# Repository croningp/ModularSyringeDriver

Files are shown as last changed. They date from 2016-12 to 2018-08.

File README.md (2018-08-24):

# Modular Syringe Driver
Welcome to the Modular Syringe Driver repository! Here, you will find all the necessary information to create your own version of this device.

Here is the finished product:

Alt img

All designs are hosted on Onshape:
* [Syringe Driver](https://cad.onshape.com/documents/56ab4447e4b0dff6d869c7ac/w/10403a3c4431f66501924e81/e/ad868b310df8ef7bb56f2516)
* [Modularity](https://cad.onshape.com/documents/20421eb13def16ddb65f3155/w/9ed7d19760b1ecfa0f48b9ff/e/2a6517c7e659cf206dda40c0)

For a list of all the materials you will need, please see the [Materials](hardware/materials.md) documentation.
* Note: A 3D printer is required to obtain some of these materials.

## Modularity
The appeal of this device is its modularity. Many different additions can be designed and printed for this device.
Here are a few examples of possible additions:



## Dependencies
* [Commanduino](https://github.com/croningp/commanduino)
* [Arduino CommandHandler](https://github.com/croningp/Arduino-CommandHandler)
* [Arduino CommandTools](https://github.com/croningp/Arduino-CommandTools)

## Assembly
Please see the the [Assembly](hardware/assembly.md) documentation for information on assembly.

## Example Usage
Below is an example of how to use [commanduino](https://github.com/croningp/commanduino) to communicate with the syringe driver.
Here we import the CommandManager which is used to communicate with the hardware via Arduino.
We also import the Axis device from Commanduino which allows the syringe to be placed on an XY axis for independent movement.

Variables are set up for the individual components of the driver, such as how many mm/step the motor should move, and the maximum volume of the syringe etc.
Instantiating an Axis object with the stepper information and passing it to the Syringe allows us full access to the Syringe commands.

See the [Syringe software](software/syringe.py) for more information on the syringe commands. 

JSON Example for setting up the Linear Accelerator Actuator in commanduino:
```json

{
  "ios" : [
    {
      "port": "/dev/tty.usbmodem1411"
    },
    {
      "port": "/dev/ttyACM0"
    },
    {
      "port": "/dev/ttyACM1"
    },
    {
      "port": "/dev/ttyACM2"
    }
  ],
  "devices": {
    "stepper": {
      "command_id": "LS1",
      "config": {
        "enabled_acceleration": false,
        "speed": 1000,
        "max_speed": 1000,
        "acceleration": 1000
      }
    }
  }
}
```

Python code for setting up the Syringe Driver: 

``` python
from commanduino import CommandManager
from commanduino.devices.axis import Axis
from syringe import Syringe

configfile = os.path.join(HERE_PATH, 'robot_config.json')
cmdMng = CommandManager.from_configfile(configfile)

MICROSTEP = 32.0
LINEAR_STEPPER_UNIT_PER_STEP = 0.05  # mm/step
SYRINGE_UNIT_PER_MM = 250 / 59.70  # 59.70mm for 250ul
SYRINGE_MAX = 235
SYRINGE_AXIS = Axis(cmdMng.S1, LINEAR_STEPPER_UNIT_PER_STEP * SYRINGUE_UNIT_PER_MM / MICROSTEP, 0, SYRINGE_MAX)
SYRINGE = Syringe(SYRINGE_AXIS, SYRINGE_MAX)
```

## Authors

Design and code by [Jonathan Grizou](http://www.chem.gla.ac.uk/cronin/members/Jonathan/), documentation by [Graham Keenan](https://github.com/ShinRa26), while working in the [Cronin Group](http://www.chem.gla.ac.uk/cronin/).

## Licenses

|   License     |     Hardware    |   Software      |
| ------------- | :-------------: | :-------------: |
| Title  | [Creatives Commons BY-SA](http://creativecommons.org/licenses/by-sa/4.0/)  |[GPL v3](http://www.gnu.org/licenses/gpl.html)  |
| Logo  |   |GPL V3 (http://www.gnu.org/licenses/gpl.html)  |

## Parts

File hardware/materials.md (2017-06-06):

# Bill of Materials
These are the materials needed to create the modular syringe driver and where to source them.

## Screws & Quantities
Screw | Quantity | Vendor
--- | --- | ---
M2.5 x 6mm | 6 | [RS Components](http://uk.rs-online.com/web/p/socket-screws/4838124/)
M3 x 6mm | 5 | [RS Components](http://uk.rs-online.com/web/p/socket-screws/1871207/)
M2.5 x 12mm | 5 | [RS Components](http://uk.rs-online.com/web/p/socket-screws/4838130/)
M3 x 10mm | 2 | [RS Components](http://uk.rs-online.com/web/p/socket-screws/2328366/)
M3 x 12mm | 4 | [RS Components](http://uk.rs-online.com/web/p/socket-screws/1871229/)

## Stepper Motor

The stepper motor used is a [custom-made Nema 11](custom_stepper/), sourced from Heason (This is the preferred motor for this setup).

Contact [Paul Sorrell](mailto:psorrell@heason.com) for more information.

Alternative motor from [Stepper Online](http://www.omc-stepperonline.com/threaded-rod-nema-11-external-linear-stepper-motor34mm-body-100mm-t5-x-2-p-203.html):



## Stop Switch
The switch used on the syringe driver is a D2F Ultra Subminature Basic Switch, sourced from [Omron](http://uk.farnell.com/omron-electronic-components/d2f01lt/microswitch-hinge-lever-0-1/dp/1961085)

[Data Sheet](https://www.omron.com/ecb/products/pdf/en-d2f.pdf) for the D2F switch.

## Arduino Mega + RAMPS Shield
The syringe driver is controlled via an Arduino Mega 2560 board fitted with a RAMPS v1.4 shield.

* The Arduino Mega can be sourced from the [Arduino website](https://www.arduino.cc/en/Main/ArduinoBoardMega2560) or from many electronics retailers.


* The RAMPS v1.4 shield can be sourced from [Ooznest](http://ooznest.co.uk/RAMPS-14-Controller-Board-Premium&currency=GBP&language=en?gclid=Cj0KEQiAyuPCBRCimuayhb3qqvwBEiQAgz62kVp1GNCQKYvTIFOcvpG9ZQ0eJvKzC2Tw6_trZBFtpCMaAlxl8P8HAQ)


## Stepper Motor Drivers for RAMPS v1.4
The stepper drivers used to control the stepper motor are [DRV8825 Drivers](https://www.pololu.com/product/2982)


Here is a video on how to tune the driver to deliver the desired Amperage: https://www.youtube.com/watch?feature=player_embedded&v=89BHS9hfSUk

## Linear Guide Rail
The syringe is guided by a linear rail, sourced at [RS Components](http://uk.rs-online.com/web/p/linear-guides-rails/6192391/)


## Linear Guide Carraige
Attached to the linear rail is a guide carraige, also sourced at [RS Components](http://uk.rs-online.com/web/p/linear-guides-guide-blocks-carriages/6192442/)


## 3D Prints
Many of the parts needed to create this driver can be 3D printed. Please see the [Basic Driver](basic_driver_stls/) and [Modular Additions](modular_additions_stls/) folders for the appropriate STL files.

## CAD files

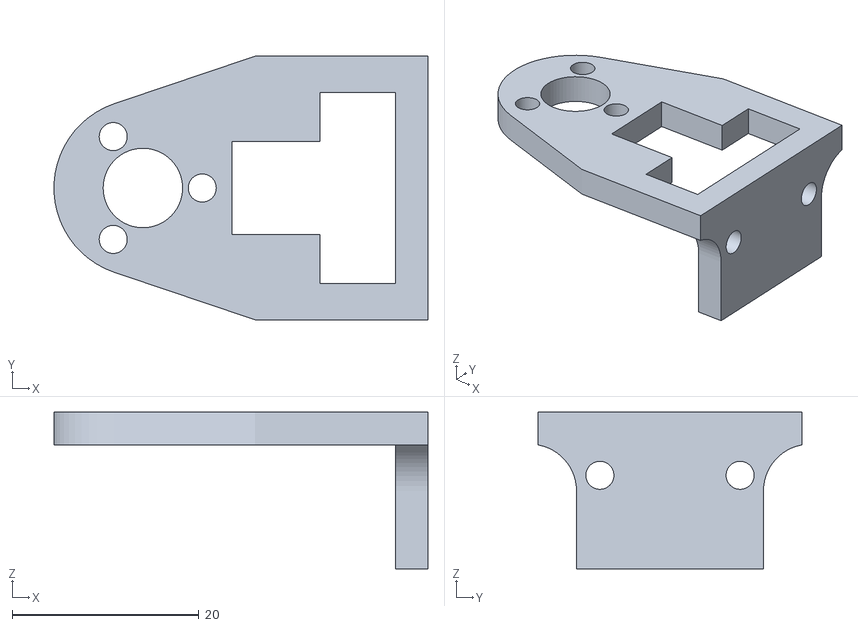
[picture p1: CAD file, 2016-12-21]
hardware/basic_driver_stls/Syringe_Holder_Carriage.stl
40.0 x 28.2 x 16.8

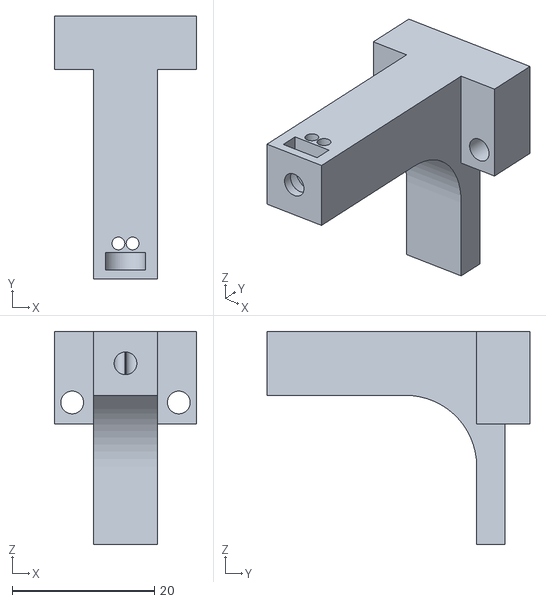
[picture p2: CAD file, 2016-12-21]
hardware/modular_additions_stls/cleaning_addon/Cleaning_Mount.stl
20.0 x 37.0 x 30.0

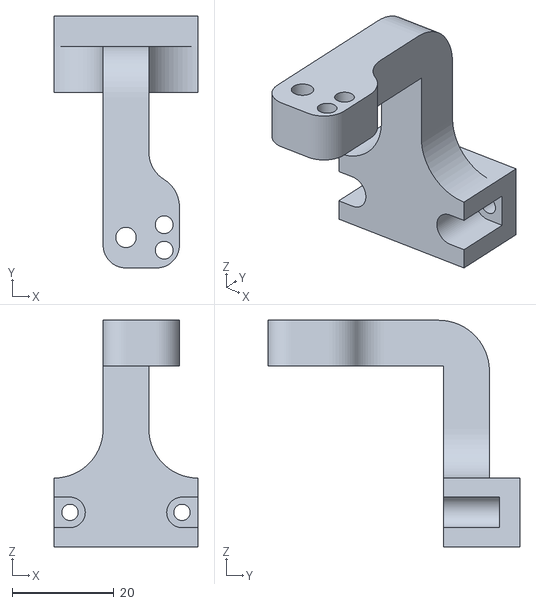
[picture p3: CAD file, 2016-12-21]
hardware/modular_additions_stls/guide_addon/Guide_v2.stl
28.2 x 49.5 x 44.5

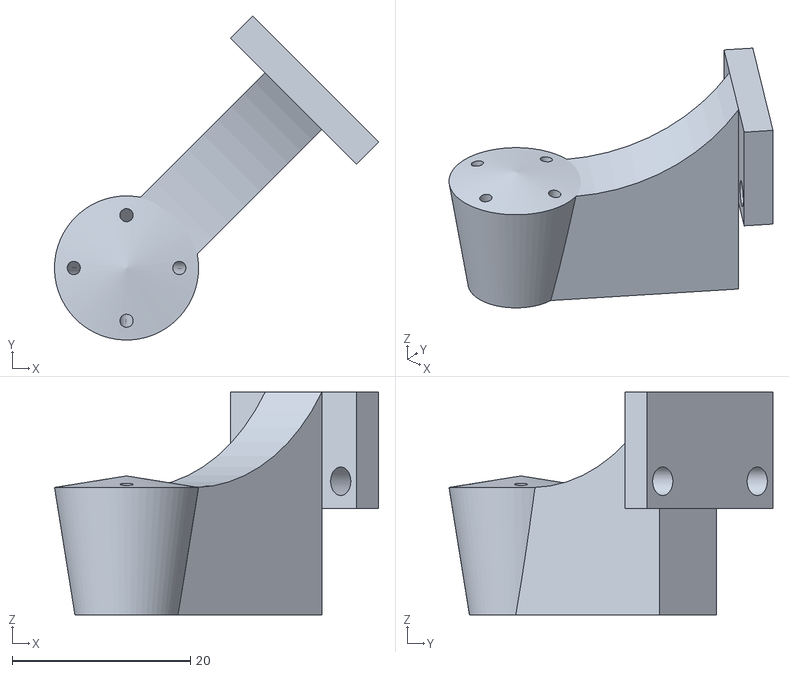
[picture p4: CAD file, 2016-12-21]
hardware/modular_additions_stls/oil_station_addon/precision_station.stl
36.4 x 36.4 x 25.0

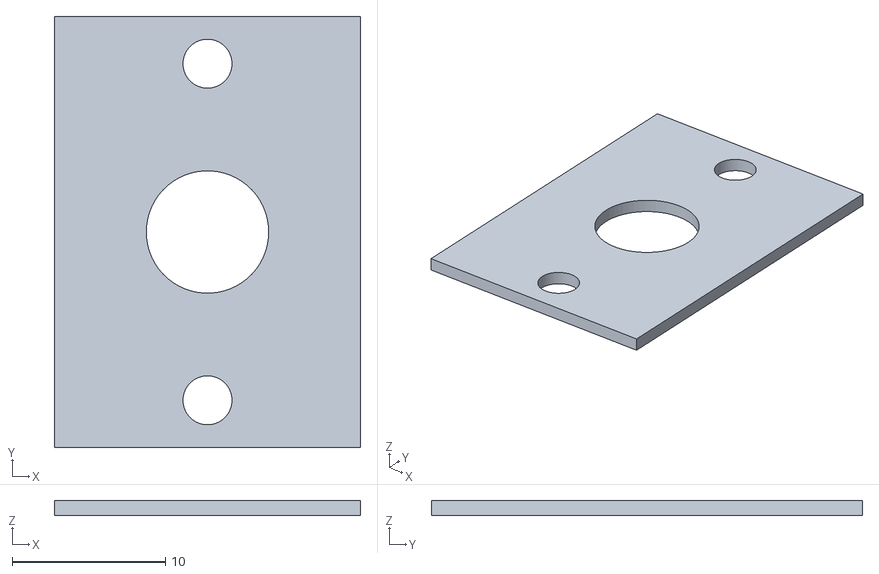
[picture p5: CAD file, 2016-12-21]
hardware/modular_additions_stls/syringe_addon/Syringe_Cover_Bottom.stl
20.0 x 28.2 x 1.00

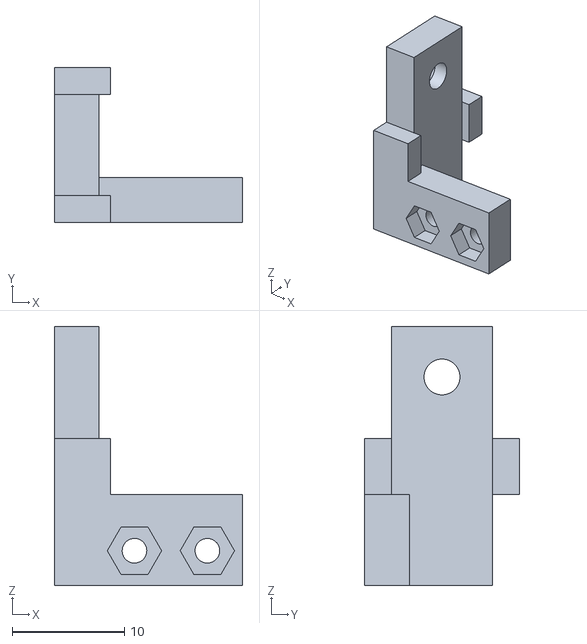
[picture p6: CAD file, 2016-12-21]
hardware/basic_driver_stls/microswitch_bracket.stl
16.8 x 13.8 x 23.1

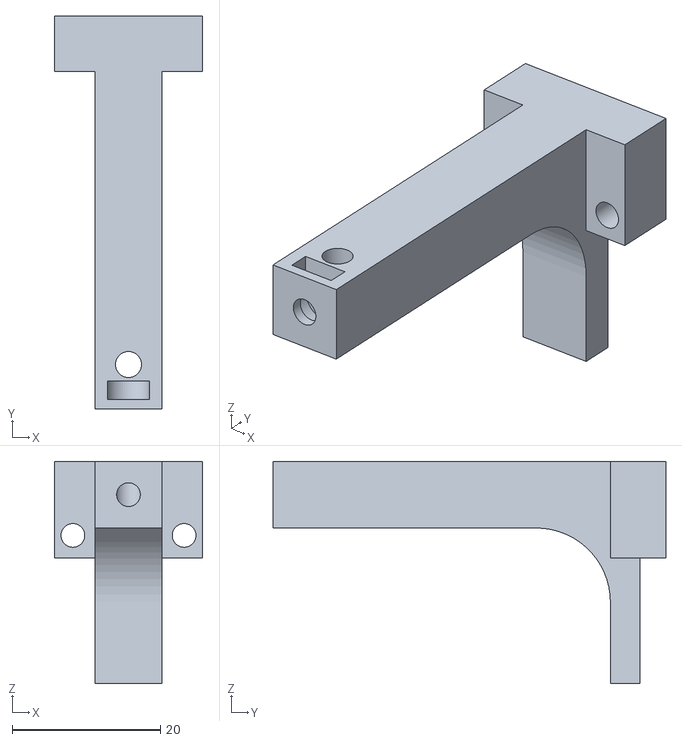
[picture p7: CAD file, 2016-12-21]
hardware/modular_additions_stls/cleaning_addon/Cleaning_mount_v2.stl
20.0 x 53.0 x 30.0

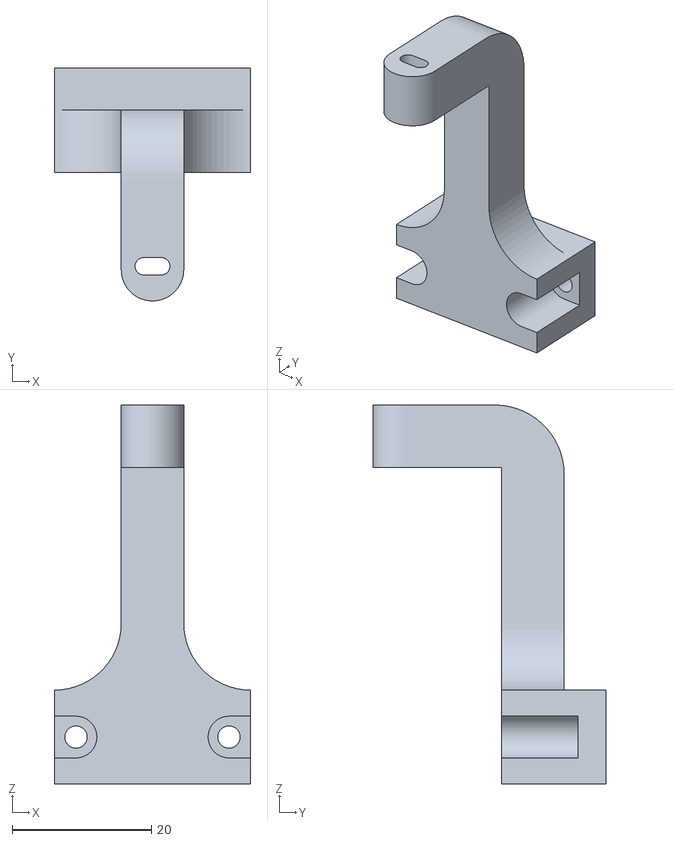
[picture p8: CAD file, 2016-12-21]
hardware/modular_additions_stls/guide_addon/Guide.stl
28.2 x 33.5 x 54.5

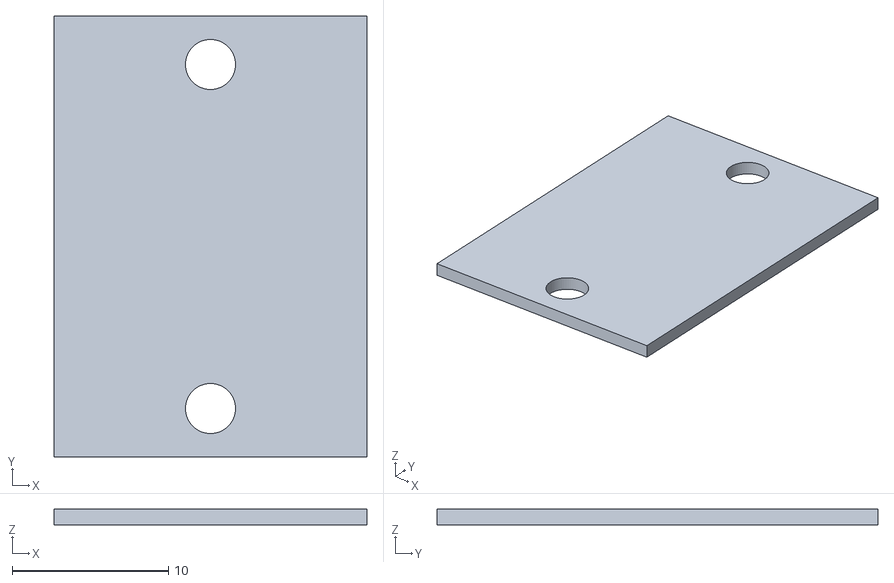
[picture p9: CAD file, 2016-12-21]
hardware/modular_additions_stls/syringe_addon/Syringe_Cover_Top.stl
20.0 x 28.2 x 1.00

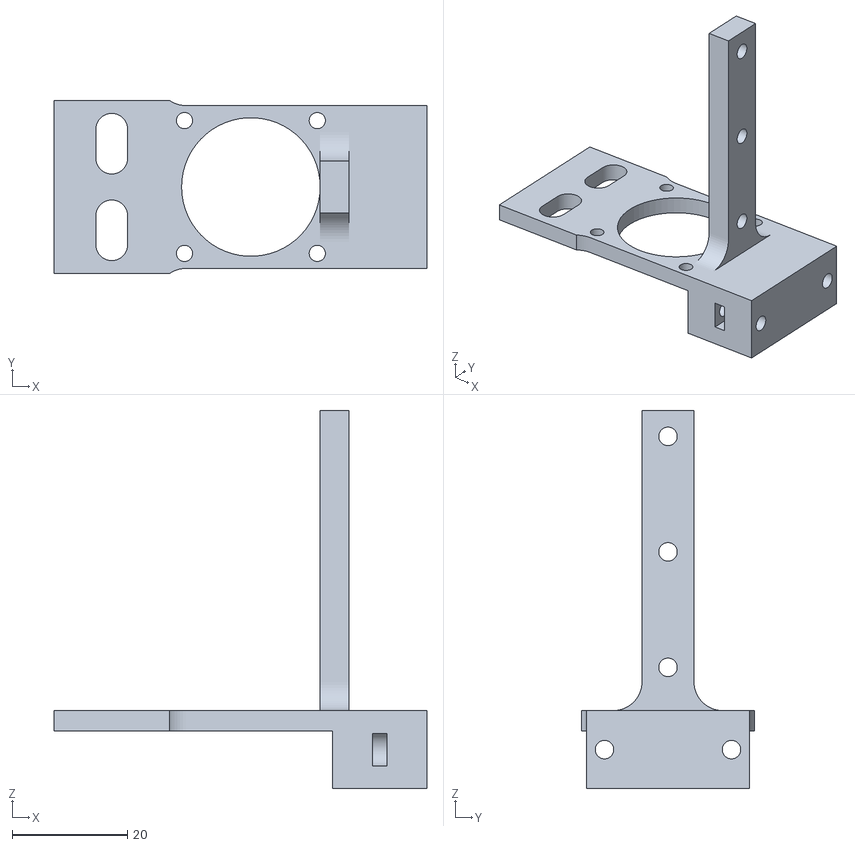
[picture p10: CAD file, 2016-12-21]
hardware/basic_driver_stls/Syringe_base.stl
64.6 x 30.0 x 65.5

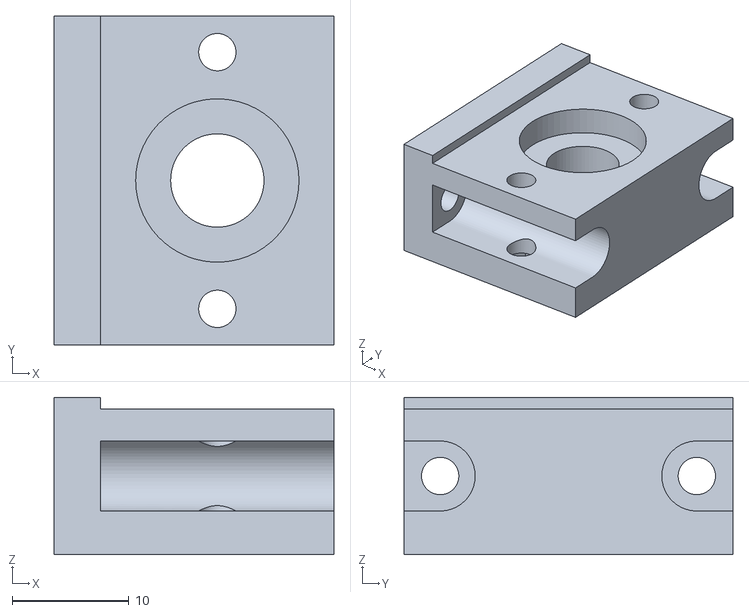
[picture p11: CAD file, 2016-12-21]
hardware/modular_additions_stls/syringe_addon/Syringe_Holder_Bottom.stl
24.0 x 28.2 x 13.5

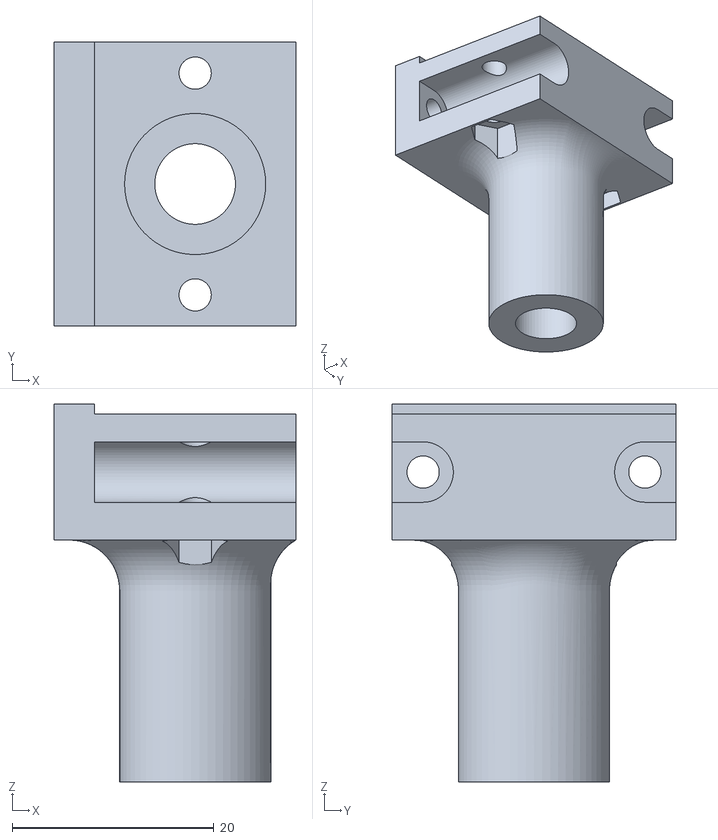
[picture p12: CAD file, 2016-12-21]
hardware/modular_additions_stls/syringe_addon/Syringe_Holder_Bottom_Extended.stl
24.0 x 28.2 x 37.5

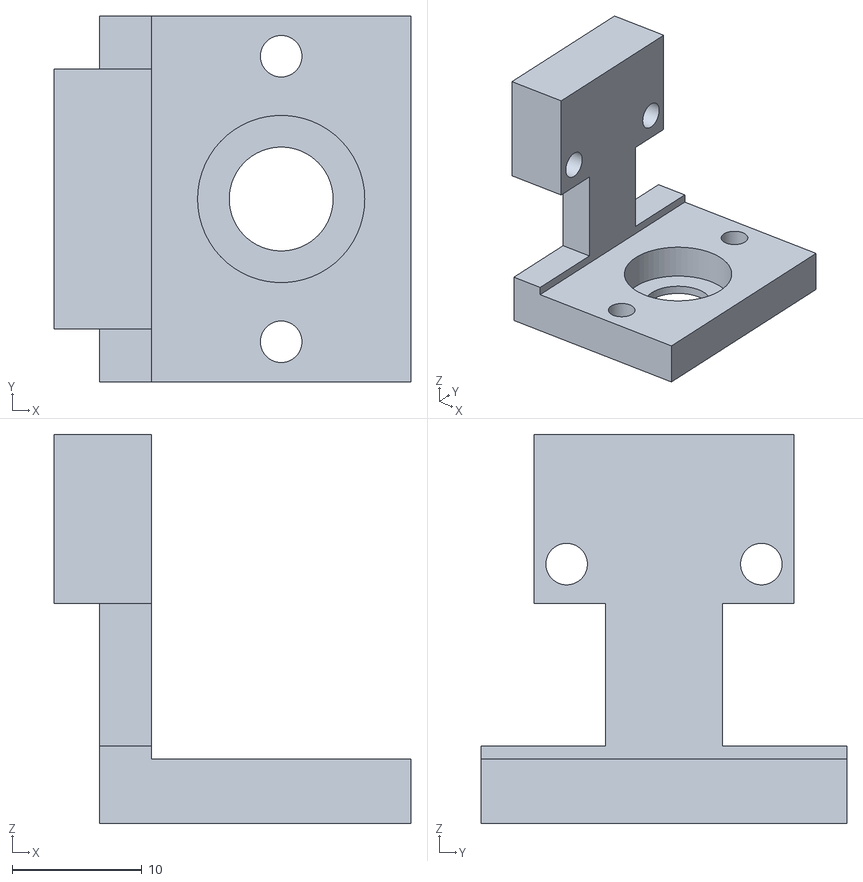
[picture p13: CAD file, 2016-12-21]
hardware/modular_additions_stls/syringe_addon/Syringe_puller.stl
27.5 x 28.2 x 30.0

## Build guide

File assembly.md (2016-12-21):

# Assembly of the Modular Syringe Driver
This purpose of this guide is to explain how to assemble the basic syringe driver.

## What you will need
In addition to the items listed in the [materials](hardware/materials.md) documentation, you will also need:

* 6x M2.5 6mm Screws 
* 5x M3 6mm Screws
* 5x M2.5 12mm Screws
* 2x M3 10mm Screws
* 4x M3 12mm Screws
* Appropriately-sized nuts for each screw type

## Part 1: Attaching the base to the motor
Requirements:
* 4x M2.5 6mm Screws
* Driver Base



Start by placing the base on top of the stepepr motor with the wires perpendicular to the base:


Screw the base onto the stepper motor:


## Part 2: Attaching the Rail + Guide
Requirements:
* 3x M3 6mm Screws
* 3x M3 Nuts
* Rail
* Rail Guide



Place the Rail against the vertical post, like so:


Add the nuts to the divots and screw in place:


Next, carefully add the Rail Guide to the rail:


## Part 3: Attaching the Frame to the Rail Guide
Requirements:
* 2x M3 6mm Screws
* Frame



Slide the frame over the rail with the vertical portion facing downwards, like so:


Screw the frame onto the bottom section of the Rail Guide


## Part 4: Securing the Frame onto the Threaded Guide:
Requirements:
* 3x M2.5 12mm Screws
* 3x M2.5 Nuts

Raise the threaded guide on the motor:


Add the screw and secure with a nut, like so:


Do this for the remaining two slots:


## Part 5: Addition of the Syringe Holder (Top)
Requirements:
* 2x M3 10mm Screws
* Syringe Holder (Top Portion)



Secure the syringe holder to the top portion of the Rail Guide, like so:


## Part 6: Addition of the Syringe Holder (Bottom)
Requirements:
* 2x M3 16mm Screws
* 2x M3 Nuts
* Syringe Holder (Bottom Portion)



Insert the two nuts into the slots on the base, added in **Part 1**


Insert the screws into the Syringe Holder:


Screw the Syringe Holder to the base:


## Part 7: Addition of the Switch
* 2x M2.5 12mm Screws
* 2x M2.5 Nuts
* Switch
* Switch Holding Bracket



Add the two nuts into the divots on the Switch Holding Bracket:


Add the two screws to the Switch:


Screw in place:


## Part 7.5: Attaching the Switch to the Rail
Requirements:
* Switch prepared from **Part 7**
* 1x M3 6mm Screw
* 1x M3 Nut



Similar to **Part 2**, attach the switch bracket to the top of the Rail:


## Part 8: Addition of the Syringe Cover (Bottom)
Requirements:
* Syringe
* Syringe Cover
* 2x M3 16mm Screws
* 2x M3 Nuts



Add the syringe - remove the plunger first - to the Holder:
**NOTE:** You may have to remove the Syringe Holder (**Part 5**) in order to fit the syringe into the holder in this section.


Add the cover:


Add the nuts to the divots on the bottom of the holder and crew in place, like so:


## Part 9: Addition of the Syringe Cover (Top)
Requirements:
* Syringe Cover (Top)
* Syringe plunger
* 2x M2.5 6mm Screws
* 2x M2.5 Nuts



Insert the plunger through the top of the Syringe Holder (Ensure the plunger is inline witht he Syringe!):


Add the Syringe Cover:


Add the nuts and screw in place:


**That's all there is to it!**

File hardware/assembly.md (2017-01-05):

# Assembly of the Modular Syringe Driver
This purpose of this guide is to explain how to assemble the basic syringe driver.

## What you will need
Please see [Bill of Materials](materials.md) for detailed listing.

Item | Quantity | Vendor
--- | --- | ---
M2.5 x 6mm Screw | 6 | [RS Components](http://uk.rs-online.com/web/p/socket-screws/4838124/)
M3 x 6mm Screw | 5 | [RS Components](http://uk.rs-online.com/web/p/socket-screws/1871207/)
M2.5 x 12mm Screw | 5 | [RS Components](http://uk.rs-online.com/web/p/socket-screws/4838130/)
M3 x 10mm Screw | 2 | [RS Components](http://uk.rs-online.com/web/p/socket-screws/2328366/)
M3 x 12mm Screw | 4 | [RS Components](http://uk.rs-online.com/web/p/socket-screws/1871229/)
Stepper Motor | 1 | See [Bill of Materials](materials.md)
Microswitch | 1 | [Omron](http://uk.farnell.com/omron-electronic-components/d2f01lt/microswitch-hinge-lever-0-1/dp/1961085)
Arduino Mega 2560 | 1 | [Arduino.cc](https://www.arduino.cc/en/Main/ArduinoBoardMega2560)
RAMPS v1.4 Shield | 1 | [Ooznest](http://ooznest.co.uk/RAMPS-14-Controller-Board-Premium&currency=GBP&language=en?gclid=Cj0KEQiAyuPCBRCimuayhb3qqvwBEiQAgz62kVp1GNCQKYvTIFOcvpG9ZQ0eJvKzC2Tw6_trZBFtpCMaAlxl8P8HAQ)
DRV8825 Stepper Driver | 1 | [Pololu](https://www.pololu.com/product/2982)
Linear Guide Rail | 1 | [RS Components](http://uk.rs-online.com/web/p/linear-guides-rails/6192391/)
Linear Guide Carriage | 1 | [RS Components](http://uk.rs-online.com/web/p/linear-guides-guide-blocks-carriages/6192442/)
3D Prints | 1x Each | [Basic Driver STLs](basic_driver_stls/), [Modular Addition STLs](modular_addition_stls/)

## Part 1: Attaching the base to the motor
Requirements:
* 4x M2.5 6mm Screws
* Driver Base



Start by placing the base on top of the stepepr motor with the wires perpendicular to the base:


Screw the base onto the stepper motor:


## Part 2: Attaching the Rail + Guide
Requirements:
* 3x M3 6mm Screws
* 3x M3 Nuts
* Rail
* Rail Guide



Place the Rail against the vertical post, like so:


Add the nuts to the divots and screw in place:


Next, carefully add the Rail Guide to the rail:


## Part 3: Attaching the Frame to the Rail Guide
Requirements:
* 2x M3 6mm Screws
* Frame



Slide the frame over the rail with the vertical portion facing downwards, like so:


Screw the frame onto the bottom section of the Rail Guide


## Part 4: Securing the Frame onto the Threaded Guide:
Requirements:
* 3x M2.5 12mm Screws
* 3x M2.5 Nuts

Raise the threaded guide on the motor:


Add the screw and secure with a nut, like so:


Do this for the remaining two slots:


## Part 5: Addition of the Syringe Holder (Top)
Requirements:
* 2x M3 10mm Screws
* Syringe Holder (Top Portion)



Secure the syringe holder to the top portion of the Rail Guide, like so:


## Part 6: Addition of the Syringe Holder (Bottom)
Requirements:
* 2x M3 16mm Screws
* 2x M3 Nuts
* Syringe Holder (Bottom Portion)



Insert the two nuts into the slots on the base, added in **Part 1**


Insert the screws into the Syringe Holder:


Screw the Syringe Holder to the base:


## Part 7: Addition of the Switch
* 2x M2.5 12mm Screws
* 2x M2.5 Nuts
* Switch
* Switch Holding Bracket



Add the two nuts into the divots on the Switch Holding Bracket:


Add the two screws to the Switch:


Screw in place:


## Part 7.5: Attaching the Switch to the Rail
Requirements:
* Switch prepared from **Part 7**
* 1x M3 6mm Screw
* 1x M3 Nut



Similar to **Part 2**, attach the switch bracket to the top of the Rail:


## Part 8: Addition of the Syringe Cover (Bottom)
Requirements:
* Syringe
* Syringe Cover
* 2x M3 16mm Screws
* 2x M3 Nuts



Add the syringe - remove the plunger first - to the Holder:
**NOTE:** You may have to remove the Syringe Holder (**Part 5**) in order to fit the syringe into the holder in this section.


Add the cover:


Add the nuts to the divots on the bottom of the holder and crew in place, like so:


## Part 9: Addition of the Syringe Cover (Top)
Requirements:
* Syringe Cover (Top)
* Syringe plunger
* 2x M2.5 6mm Screws
* 2x M2.5 Nuts



Insert the plunger through the top of the Syringe Holder (Ensure the plunger is inline witht he Syringe!):


Add the Syringe Cover:


Add the nuts and screw in place:


To ensure the nuts are secured in place, add some Screw Lock glue to the nuts:


## Cabling the Microswitch
* The convention for the Microswitch is:
    * Red: 5v
    * Black: Ground
    * Blue: Signal



The order, from left to right, is as follows:
* Left Pin: Blue(Signal)
* Middle Pin: Black (Ground)
* Right Pin: Red (5v Power)



## Cabling the Stepper Motor
* The stepper motor comes with 4 wires:
    * Red
    * Red/White
    * Green
    * Green/White

To connect them to the ramps shield, the convention is as follows (Motor -> RAMPS connector):
* Red/White -> Black
* Red -> Green
* Green/White -> Red
* Green -> Blue

Example:


Attaching to the RAMPS shield (also applies to the Microswitch):


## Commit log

2016-12-20 Added the bill of materials
2016-12-21 First pass
    [Cleaning_Mount.stl, Cleaning_mount_v2.stl, Guide.stl, Guide_v2.stl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]
2016-12-21 Minor changes
    [Cleaning_Mount.stl, Cleaning_mount_v2.stl, Guide.stl, Guide_v2.stl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]
2016-12-21 Minor updates
    [Syringe_Cover_Bottom.stl, Syringe_Cover_Top.stl, Syringe_Holder_Bottom.stl, Syringe_Holder_Bottom_Extended.stl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]
2017-01-05 Added the wiring and JSON exmaple

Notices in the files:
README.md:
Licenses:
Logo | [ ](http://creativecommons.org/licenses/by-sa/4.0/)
